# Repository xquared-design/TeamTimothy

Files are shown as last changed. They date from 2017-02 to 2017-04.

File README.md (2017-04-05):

# TeamTimothy
## Table of Contents
1. Intro
2. Components
3. License Terms
4. Connecting to the Pi Zero

## Intro
This project started as a part of [Makers Making Change Access Makeathon](http://www.makersmakingchange.com/accessmakeathonsummary/), an initiative of the [Neil Squire Society](http://www.neilsquire.ca).
The goal is to help Timothy, a 10 year-old boy with ataxia, play his favourite games on Wii console. This project involves modifying a standard Nintendo Wii Remote and Nunchuk by replacing the buttons and joystick with larger versions and positioning them in a more ergonomic arrangement. The factory PCBs from the controllers are retained and new inputs wired to them. The code is executed using a Raspberry Pi Zero with Raspbian. 

## Components
For a full list of components used, see the bill of materials [here](BOM.md).

## License Terms
All hardware is licensed under [Attribution-ShareAlike 4.0 International (CC BY-SA 4.0)](https://creativecommons.org/licenses/by-sa/4.0/) and all software is licensed under [GNU Lesser General Public License v3.0 (GNU LGPLv3)](https://choosealicense.com/licenses/lgpl-3.0/).

## Additional Details
For more information, such as how to connect to the Raspberry Pi Zero, please check out the [wiki](https://github.com/xquared-design/TeamTimothy/wiki).

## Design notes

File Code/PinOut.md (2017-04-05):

# RPi Zero GPIO Pinout Mapping

## Inputs

### Red buttons
Button | Physical Pin # | (BCM) Pin Name.
--- | --- | ---
1 | 11 | GPIO17
2 | 13 | GPIO27
3 | 15 | GPIO22 
4 | 29 | GPIO5 
5 | 31 | GPIO6

### Joystick button
Button | Physical Pin # | (BCM) Pin Name.
--- | --- | ---
6 | 37 | GPIO26

## Outputs (WiiMote buttons)

Button | Physical Pin # | (BCM) Pin Name.
--- | --- | ---
A | 12 | GPIO18
B | 16 | GPIO23
C | 18 | GPIO24 
Z | 22 | GPIO25
 
## VCC and GND Connections

Purpose | Physical Pin #s | (BCM) Pin Name.
--- | --- | ---
Power WiiMote | 1, 17| 3.3V
Ground WiiMote| 9, 25, 39 | GND 

Check out [pinout.xyz](https://pinout.xyz/#) for an interactive pinout diagram and [this sparkfun tutorial](https://learn.sparkfun.com/tutorials/raspberry-gpio) for a detailed explanation of GPIO on the Raspberry Pi.

## Nominal button functions from left to right

C button will be in joystick (button 6)

A, B, Combo 1, Combo 2, Z (buttons 1-5)

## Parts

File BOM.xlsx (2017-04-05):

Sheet: Mechanical
PART | PART DESCRIPTION | QUANTITY | SUPPLIER | PART NUMBER | SUPPLIER LINK | UNIT PRICE | ALT. SUPPLIER | MANUFACTURER LINK
Push button switch PS-300C1 | SPDT momentary contact On-(On) microswitch, red and white | 5 | Lee's Electronic | PB-300-C1 | http://leeselectronic.com/en/product/3290.html | $6.60 | - | http://php2.twinner.com.tw/site/product_classify/chn-List-fe-fe1/See_Catelog.php?case=71821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
Sanwa JLF-TP-8YT-SK joystick | 4 & 8 Way adjustable OEM arcade joystick, green ball handle | 1 | Amazon.com | JLF-TP-8YT-SK | - | 22.92 USD | Amazon.ca | -
Micro switch DM1-03 long lever | Joystick top push button | 1 | Lee's Electronic | DM1-03 | http://leeselectronic.com/en/product/347.html | $2.95 | Newark.com | -
4 mm screws |  | 4 | - | - | - | - | - | -
4 mm nuts |  | 4 | - | - | - | - | - | -

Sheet: Electrical
PART | PART DESCRIPTION | QUANTITY | SUPPLIER | PART NUMBER | SUPPLIER LINK | UNIT PRICE | ALT. SUPPLIER | MANUFACTURER LINK
Raspberry Pi Zero | - | 1 | CanaKit | - | http://www.canakit.com/raspberry-pi-zero.html | $6.75 | Adafruit | https://www.raspberrypi.org/products/pi-zero/
Pivos Moju 2600mAh Mobile Charger | USB Rechargeable Power Bank - White | 1 | NCIX | PTGMPBM2-W | http://www.ncix.com/detail/pivos-moju-2600mah-mobile-charger-37-99830.htm | $7.99 | NCIX US | http://global.pivosgroup.com/a-home-for-moju-battery/
Nintendo Wii Remote | - | 1 | - | - | - | - | - | -
Nintendo Nunchuk Controller | - | 1 | - | - | - | - | - | -
Kingston 32GB microSDHC Class 10 card | microSD card with Raspbian Jessie lite loaded | 1 | NCIX | SDC10G2/32GBCR | http://www.ncix.com/detail/kingston-sdc10g2-32gbcr-32gb-microsdhc-class-06-117882.htm?promoid=1637 | $18.60 | Newegg | https://www.kingston.com/en/flash/microsd_cards
Ribbon cable with 40 pin IDC connector | - | 1 | - | - | - | - | - | -

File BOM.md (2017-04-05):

#Bill of Material
Here you will find all the components listed in [BOM.xlsx](BOM.xlsx?raw=true) presented for your convenience.
##Mechanical
| PART                           | PART DESCRIPTION                                            |   QUANTITY | SUPPLIER         | PART NUMBER   | SUPPLIER LINK                                  | UNIT PRICE   | ALT. SUPPLIER   | MANUFACTURER LINK                                                                                                                                                  |
|:-------------------------------|:------------------------------------------------------------|-----------:|:-----------------|:--------------|:-----------------------------------------------|:-------------|:----------------|:-------------------------------------------------------------------------------------------------------------------------------------------------------------------|
| Push button switch PS-300C1    | SPDT momentary contact On-(On) microswitch, red and white   |          5 | Lee's Electronic | PB-300-C1     | http://leeselectronic.com/en/product/3290.html | 6.6          | -               | http://php2.twinner.com.tw/site/product_classify/chn-List-fe-fe1/See_Catelog.php?case=71821&part_no=PB-300-,C1&Company_SN=692&PHPSESSID=bav8rj2u74lha3c19bh2fokih0 |
| Sanwa JLF-TP-8YT-SK joystick   | 4 & 8 Way adjustable OEM arcade joystick, green ball handle |          1 | Amazon.com       | JLF-TP-8YT-SK | -                                              | 22.92 USD    | Amazon.ca       | -                                                                                                                                                                  |
| Micro switch DM1-03 long lever | Joystick top push button                                    |          1 | Lee's Electronic | DM1-03        | http://leeselectronic.com/en/product/347.html  | 2.95         | Newark.com      | -                                                                                                                                                                  |
| 4 mm screws                    |                                                             |          4 | -                | -             | -                                              | -            | -               | -                                                                                                                                                                  |
| 4 mm nuts                      |                                                             |          4 | -                | -             | -                                              | -            | -               | -                                                                                                                                                                  |
##Electrical
| PART                                   | PART DESCRIPTION                              |   QUANTITY | SUPPLIER   | PART NUMBER    | SUPPLIER LINK                                                                                      | UNIT PRICE   | ALT. SUPPLIER   | MANUFACTURER LINK                                     |
|:---------------------------------------|:----------------------------------------------|-----------:|:-----------|:---------------|:---------------------------------------------------------------------------------------------------|:-------------|:----------------|:------------------------------------------------------|
| Raspberry Pi Zero                      | -                                             |          1 | CanaKit    | -              | http://www.canakit.com/raspberry-pi-zero.html                                                      | 6.75         | Adafruit        | https://www.raspberrypi.org/products/pi-zero/         |
| Pivos Moju 2600mAh Mobile Charger      | USB Rechargeable Power Bank - White           |          1 | NCIX       | PTGMPBM2-W     | http://www.ncix.com/detail/pivos-moju-2600mah-mobile-charger-37-99830.htm                          | 7.99         | NCIX US         | http://global.pivosgroup.com/a-home-for-moju-battery/ |
| Nintendo Wii Remote                    | -                                             |          1 | -          | -              | -                                                                                                  | -            | -               | -                                                     |
| Nintendo Nunchuk Controller            | -                                             |          1 | -          | -              | -                                                                                                  | -            | -               | -                                                     |
| Kingston 32GB microSDHC Class 10 card  | microSD card with Raspbian Jessie lite loaded |          1 | NCIX       | SDC10G2/32GBCR | http://www.ncix.com/detail/kingston-sdc10g2-32gbcr-32gb-microsdhc-class-06-117882.htm?promoid=1637 | 18.6         | Newegg          | https://www.kingston.com/en/flash/microsd_cards       |
| Ribbon cable with 40 pin IDC connector | -                                             |          1 | -          | -              | -                                                                                                  | -            | -               | -                                                     |

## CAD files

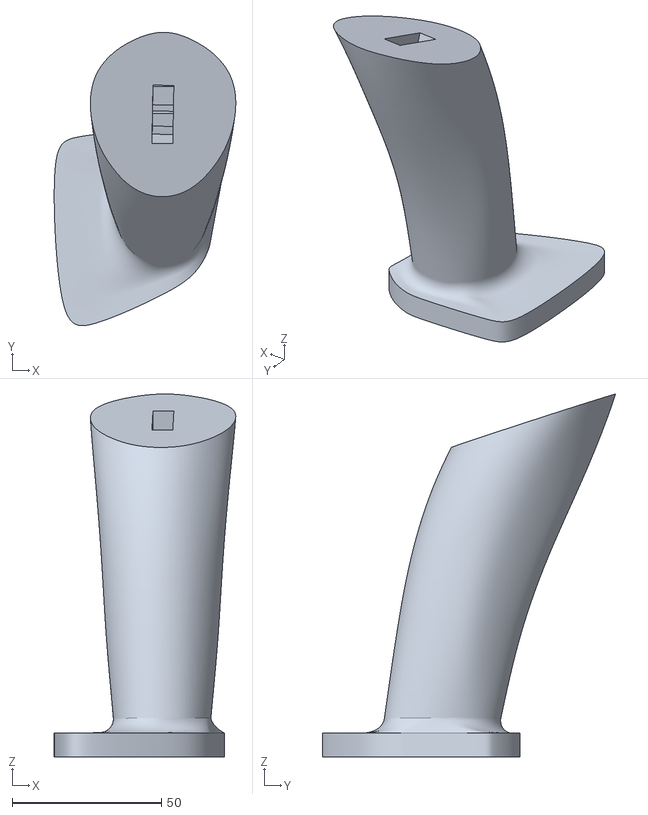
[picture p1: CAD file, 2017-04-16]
mechanical/joystick_shorter v32.stl
60.8 x 98.1 x 121.4

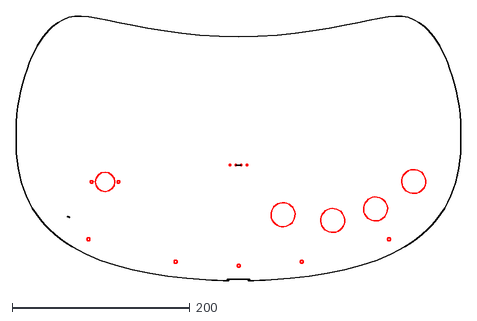
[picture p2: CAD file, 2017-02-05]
mechanical/topcover.dxf
499.9 x 297.3

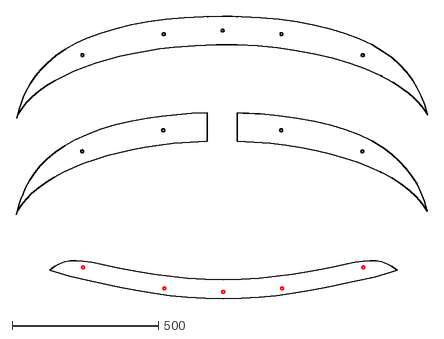
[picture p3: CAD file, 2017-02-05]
mechanical/bottom_layers.dxf
1404.3 x 964.5

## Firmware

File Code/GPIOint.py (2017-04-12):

import RPi.GPIO as GPIO
import time
import threading
import os
GPIO.setmode(GPIO.BCM) #use BCM numbering scheme

#threadList = []


DictIn = {1:17,2:27,3:22,4:5,5:6,6:26}
DictOut = {'A':18,'B':23,'C':25,'Z':24}
WII_A = DictOut['A']
WII_B = DictOut['B']
WII_C = DictOut['C']
WII_Z = DictOut['Z']



#map buttons to BCM pins per PinOut.md
for key in DictIn:
    GPIO.setup(DictIn[key], GPIO.IN, pull_up_down=GPIO.PUD_UP)

for key in DictOut:
    GPIO.setup(DictOut[key], GPIO.OUT, initial=GPIO.HIGH)

GPIO.setup(20, GPIO.OUT, initial=GPIO.LOW) #setup power on indicator light
GPIO.setup(16, GPIO.IN, pull_up_down=GPIO.PUD_UP) #setup shutdown btn

comboLookup = {17:[0,WII_A], 27:[1,WII_A, 0.250, WII_A, 0.250, WII_B, 0.250],22:[0, WII_Z],5:[0, WII_B],6:[1, WII_A, 0.250, WII_A, 0.250], 26:[0, WII_C]}

#when an input pin is called, toggle the corresponding output pin ON (LOW) and OFF
def thread_seqMacro(pin):
    for i in range(1, len(comboLookup[pin]), 2): #iterate through the list of btns, starting from 1, skipping over the durations
        GPIO.output(comboLookup[pin][i],GPIO.LOW)
        print "pulling",  "low"
        dur = comboLookup[pin][i+1]
        time.sleep(dur)
        GPIO.output(comboLookup[pin][i],GPIO.HIGH)
        print "returning",  "high"
        time.sleep(0.1)

def callback_btnPress(pin):
    #GPIO.output(18, GPIO.LOW)
    if not GPIO.input(pin):
        print "btn %d pressed" % pin
        if comboLookup[pin][0]==0:
            GPIO.output(comboLookup[pin][1:],GPIO.LOW)
        elif comboLookup[pin][0]==1:
            t=threading.Thread(target=thread_seqMacro, args=(pin,),name="macroThread")
            t.start()
#            if threadList
#                lastCombo=threadList.pop()
#                lastCombo
#            threadList.appedn(t)
    else:
        print "btn %d released" % pin
        if comboLookup[pin][0]==0:
            GPIO.output(comboLookup[pin][1:], GPIO.HIGH)
        # elif comboLookup[pin][0]==1:s

# def callback_btnRelease(pin):
#    print "btn %d released" % pin



def callback_btnShutdown(pin):
    t=threading.Thread(target=thread_wait4ShutDown, args=(pin,),name="shutdownThread")
    t.start()

def thread_wait4ShutDown(pin):
    time.sleep(3) #wait for three second
    if not GPIO.input(pin): #if button still held down, initiate shutdown sequence
        GPIO.cleanup()           # clean up GPIO on shutdown
        os.system("sudo shutdown -h now")


#def callback_btn27(channel):
#    GPIO.output(23, GPIO.LOW)
#    print "btn2 pressed, activating 23"
#    GPIO.output(23, GPIO.HIGH)
#
#def callback_btn22(channel):
#    GPIO.output(18, GPIO.LOW)
#    GPIO.output(23, GPIO.LOW)
#    print "btn3 pressed, activating both 18 and 23"
#    GPIO.output(18, GPIO.HIGH)
#    GPIO.output(23, GPIO.HIGH)

for key in DictIn:
    GPIO.add_event_detect(DictIn[key], GPIO.BOTH, callback=callback_btnPress,bouncetime=50)
    #GPIO.add_event_detect(DictIn[key], GPIO.RISING, callback=callback_btnRelease,bouncetime=300)

GPIO.add_event_detect(16, GPIO.FALLING, callback=callback_btnShutdown, bouncetime=300)

GPIO.output(20,GPIO.HIGH)

try:
    while True:
        time.sleep(1e6)
except KeyboardInterrupt:
    GPIO.cleanup()       # clean up GPIO on CTRL+C exit

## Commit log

2017-02-05 added dxf drawings used in the laser cutting of the current design
    [bottom_layers.dxf, topcover.dxf]
2017-02-07 testing out commit tool chainOn branch master
    [BOM.xlsx]
2017-02-07 debugging pre-commit hook
    [BOM.xlsx]
2017-02-07 Updated BOM to include a sheet on Electrical, to be populated later
    [BOM.xlsx]
2017-02-07 updated BOM.xlsx
    [BOM.xlsx]
2017-02-14 added GPIOint.py, currently has three input and two output
2017-03-06 updated BOM with electrical component
    [BOM.xlsx]
2017-03-08 Added joystick STL file
    [joystick.stl]
2017-03-10 updated pin mapping for output
2017-03-10 Created pinout document.
    bare minimum info on connector pinout to help with wiring. Schematic to come
2017-03-19 changed BOM.md format and content
    changed BOM format to highlight most relevant information, and added
    content in appropriate categories
    [BOM.xlsx]
2017-03-20 deleted for upload of new version
    [joystick.stl]
2017-03-20 uploaded shorter+tweaked joystick version
    shorter to be more comfortable to hold, wider shaft hole, rounder handle, other tweaks
    [joystick_shorter v31.stl]
2017-04-09 changed callback_btnPress to not start a new thread with every button press
    now wii output are pulled low for the entire duration fo the btn press
2017-04-09 changed comboLookup dictionary format to include combo type. currently, the first element denotes the type of button. 0 is a press and hold and 1 is a sequential combo
    thread_outputMarcro is now renamed thread_seqMacro in anticipation of future repeat press and concurrent press combos.
    sequential combo format as thus Pin: [1,outputPin1,duration1,outputPin2,duration2 ...]
    duration specified in seconds
    TODO: need to implement a custom thread that allows to be killed externally
2017-04-11 Fixed combo keys based on testing with Timothy.
    also added a threaded call back for shut down button, so it has to be held down for 3 seconds in order to turn off the pi zero unit
2017-04-16 Delete joystick_shorter v31.stl
    deleted in prep for updated file version
    [joystick_shorter v31.stl]
2017-04-16 Uploaded joystick_shorter v32.stl
    new version of joystick with hole to fit 0.375" shaft and larger button cutout
    [joystick_shorter v32.stl]
